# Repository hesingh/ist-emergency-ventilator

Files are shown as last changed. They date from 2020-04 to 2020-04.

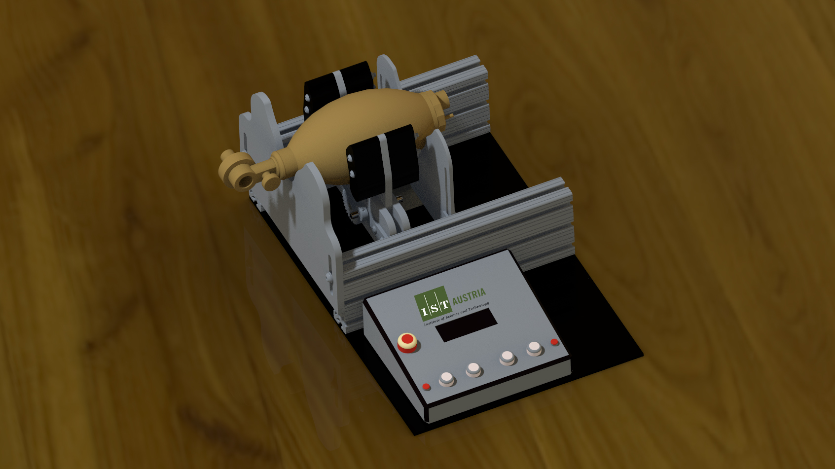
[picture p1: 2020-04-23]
Mechanical/Picture_3D_Model/bild_3_1.jpg

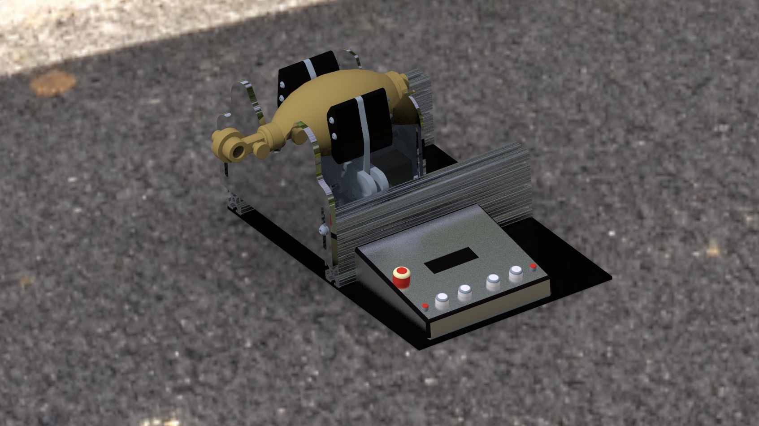
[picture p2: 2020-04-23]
Mechanical/Creo 6.0/creo.jpg

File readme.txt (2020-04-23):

ABOUT:
The enclosed files belong to the eVent IST ventilator project, inspired by the MIT E-Vent project (see https://e-vent.mit.edu/). We developed the ventilator system using technical documentation of MIT, infrastructure of IST AUSTIRA and consulting of three medical practitioners. We developed and built with great care and focus on stability and safety, still the device is not certified and not built according to all applicable regulations. Please note that this is work in progress and has never been tested on a human. The goal of the eVent IST ventilator project is to provide a simple and fast to replicate system for emergency response, and was created in reaction to the COVID-19 crisis early 2020. Furthermore, its intention is not to replace common ventilator systems, but to bridge a situation where not enough conventional machines are available.

ATTRIBUTION:
Please notice that the eVent IST ventilator was developed using the information shared by the Massachusetts Institute of Technology (MIT). You can find information on the original MIT E-Vent project under https://e-vent.mit.edu/. All Terms of Use, found here: https://e-vent.mit.edu/terms-and-conditions/, concerning the original MIT content do apply.
3rd party libraries used: Encoder by Paul Stoffregen (https://github.com/PaulStoffregen/Encoder), LiquidCrystal (https://github.com/arduino-libraries/LiquidCrystal).

FOLDERS:

	Folder name	Description							Origin
	------------------------------------------------------------------------------------------------
	Electronics	contains files for the electronic parts of the ventilator	mostly MIT E-Vent
	License		contains relevant license files					https://opensource.org
	Mechanical	contains files for the mechanical parts of the ventilator	mostly MIT E-Vent
	Pictures	contains pictures of the machine				IST AUSTRIA
	Software	contains files for the software of the ventilator		IST AUSTRIA

COPYRIGHT AND LICENSE: 
Selected Content may be downloaded by you pursuant to these Terms of Use. All copyright in and to the original MIT E-Vent Design Specifications belong to MIT. MIT is making the Design Specifications freely available to you to use, subject to these Terms of Use and your agreement to give full attribution to MIT should you reproduce, display, disseminate, or distribute the Design Specifications. All copyright in and to content going beyond the MIT E-Vent Design Specifications, and especially the software, belong to IST AUSTRIA. If and to the extent you provide any feedback, suggestions, recommendations, analysis or other information or data to IST in connection with your use of the Content (“Feedback”), you hereby permit IST to use, reproduce, disclose, distribute, modify, and prepare derivative works of such Feedback for any purpose whatsoever in perpetuity. Any downloadable software is subject to the MIT Open Source license, found here: https://opensource.org/licenses/MIT.
3rd party libraries included: Encoder: (MIT License), LiquidCrystal: LGPL License v3 (https://opensource.org/licenses/LGPL-3.0).

DISCLAIMER OF WARRANTIES
YOU ACKNOWLEDGE THAT THE CONTENT IS IN RESEARCH PHASE AND ALL OUTCOMES FROM USE OF THE CONTENT ARE NOT KNOWN. YOUR USE OF THE CONTENT, INCLUDING THE DESIGN SPECIFICATIONS AND THE SOFTWARE, IS AT YOUR OWN RISK. THE CONTENT, INCLUDING THE DESIGN SPECIFICATIONS AND THE SOFTWARE, ARE PROVIDED ON AN “AS IS” AND “AS AVAILABLE” BASIS. 
IST AUSTRIA, ON BEHALF OF ITSELF AND ITS COLLABORATORS, MAKES NO REPRESENTATIONS, WARRANTIES OR COVENANTS, WHETHER STATUTORY, EXPRESS, IMPLIED, BY COURSE OF COMMUNICATION OR DEALING, OR OTHERWISE WITH RESPECT TO THE CONTENT, INCLUDING THE DESIGN SPECIFICATIONS AND THE SOFTWARE, AND ANY RESULTING DEVICE.  IST AUSTRIA, ON BEHALF OF ITSELF AND ITS COLLABORATORS, SPECIFICALLY DISCLAIMS ANY WARRANTY WITH REGARD TO FITNESS FOR ANY PARTICULAR PURPOSE, MERCHANTABILITY OR NON-INFRINGEMENT.
WITHOUT LIMITING THE GENERALITY OF THE FOREGOING, IST AUSTRIA, ON BEHALF OF ITSELF AND ITS COLLABORATORS, MAKES NO WARRANTY OF ANY KIND THAT THE CONTENT, INCLUDING THE DESIGN SPECIFICATIONS AND THE SOFTWARE, AND ANY RESULTING DEVICE OR THE RESULTS OF THE USE OF SUCH DEVICE WILL MEET YOUR OR ANY THIRD PARTY’S REQUIREMENTS, OR ACHIEVE ANY INTENDED RESULT OR THAT THE USE OF THE DESIGN SPECIFICATIONS AND THE SOFTWARE TO MAKE A DEVICE WILL COMPLY WITH INTERNATIONAL, FEDERAL, STATE OR MUNICIPAL LAWS AND REGULATIONS REGARDING MEDICAL DEVICES OR MEDICAL USES.  YOU EXPRESSLY ACKNOWLEDGE AND AGREE THAT IST AUSTRIA, ON BEHALF OF ITSELF AND ITS COLLABORATORS, IS NOT RESPONSIBLE FOR ANY HEALTH PROBLEMS, INJURIES OR DEATH THAT MAY RESULT FROM YOUR OR ANY THIRD PARTY’S USE OF ANY DEVICE RESULTING FROM YOUR USE OF THE CONTENT, INCLUDING THE DESIGN SPECIFICATIONS AND THE SOFTWARE.  IT IS UNDERSTOOD THAT IST AUSTRIA DOES NOT PROVIDE MEDICAL OR OTHER HEALTH-RELATED ADVICE.     
IST AUSTRIA, ON BEHALF OF ITSELF AND ITS COLLABORATORS, DISCLAIMS ANY RESPONSIBILITY FOR OR ASSURANCES REGARDING THE QUALITY, FUNCTIONALITY, OR SAFETY OF ANY DEVICE RESULTING FROM YOUR USE OF THE CONTENT, INCLUDING THE DESIGN SPECIFICATIONS AND THE SOFTWARE, OR ANY DEFECT, ERRORS OR MALFUNCTION IN CONNECTION THEREWITH.  FURTHER, IST AUSTRIA, ON BEHALF OF ITSELF AND ITS COLLABORATORS, DISCLAIMS ANY RESPONSIBILITY FOR OR ASSURANCES REGARDING ANY COMMENTS, FEEDBACK, INFORMATION OR OTHER KNOW-HOW PROVIDED BY ANY USER. YOU RELY ON USER COMMENTS, FEEDBACK, INFORMATION AND/OR KNOW-HOW SOLELY AT YOUR OWN RISK. 
YOU UNDERSTAND AND ACKNOWLEDGE THAT: YOU ARE A LEARNED INDIVIDUAL THAT HAS HAD THE OPPORTUNITY TO OBTAIN ANY AND ALL INFORMATION RELEVANT TO THE USE OF ANY DEVICE RESULTING FROM YOUR USE OF THE CONTENT, INCLUDING THE DESIGN SPECIFICATIONS AND THE SOFTWARE; YOU HAVE NO OBLIGATION TO USE THE CONTENT, THE DESIGN SPECIFICATIONS AND THE SOFTWARE OR ANY DEVICE RESULTING THEREFROM AND YOU DO SO IN YOUR SOLE DISCRETION; YOU ARE RESPONSIBLE FOR DETERMINING THE DEGREE OF MONITORING OR OVERSIGHT THAT IS APPROPRIATE IN CONNECTION WITH PATIENT CARE AND THE USE OF ANY DEVICE RESULTING FROM YOUR USE OF THE CONTENT, INCLUDING THE DESIGN SPECIFICATIONS AND THE SOFTWARE; YOU HAVE ACCEPTED ALL RESPONSIBILITY AND IST AUSTRIA, ON BEHALF OF ITSELF AND ITS COLLABORATORS, RETAINS NO RESPONSIBILITY FOR YOUR USE OF ANY RESULTING DEVICE; AND YOU WILL COMPLY WITH ALL LAWS AND GOVERNMENTAL RULES, REGULATIONS AND GUIDELINES, INCLUDING ANY SAFETY PRECAUTIONS, THAT ARE APPLICABLE TO THE DEVICE OR THE USE THEREOF.
IST AUSTRIA does not guarantee or warrant that files available for downloading from the Internet or the Site will be free of viruses or other destructive code. NEITHER IST AUSTRIA NOR ANY PERSON ASSOCIATED WITH IST AUSTRIA MAKES ANY WARRANTY OR REPRESENTATION WITH RESPECT TO THE SECURITY, RELIABILITY, QUALITY, OR AVAILABILITY OF THE SITE AND THE CONTENT. IST AUSTRIA WILL NOT BE LIABLE FOR ANY LOSS OR DAMAGE CAUSED BY A DISTRIBUTED DENIAL-OF-SERVICE ATTACK, VIRUSES OR OTHER TECHNOLOGICALLY HARMFUL MATERIAL THAT MAY INFECT YOUR COMPUTER EQUIPMENT, COMPUTER PROGRAMS, DATA OR OTHER PROPRIETARY MATERIAL DUE TO YOUR USE OF THE CONTENT, YOUR DOWNLOADING OF ANY AVAILABLE CONTENT, OR YOUR USE OF ANY WEBSITE LINKED TO THE CONTENT.  

LIMITATION OF LIABILITY
TO THE FULLEST EXTENT ALLOWABLE BY LAW, IN NO EVENT WILL IST AUSTRIA, ITS TRUSTEES, DIRECTORS, OFFICERS, FACULTY, STUDENTS, EMPLOYEES, AGENTS, AFFILIATES, VOLUNTEERS, AND COLLABORATORS AND THEIR RESPECTIVE SUCCESSORS, HEIRS AND ASSIGNS BE LIABLE OR RESPONSIBLE FOR, OR INDEMNIFY YOU OR ANY THIRD PARTY FOR, DIRECT, INDIRECT, SPECIAL, INCIDENTAL, CONSEQUENTIAL, PUNITIVE OR EXEMPLARY DAMAGES OF ANY KIND, UNDER ANY LEGAL THEORY, ARISING OUT OF OR IN CONNECTION WITH YOUR USE, OR INABILITY TO USE, THE CONTENT (INCLUDING THE DESIGN SPECIFICATIONS AND THE SOFTWARE), ANY WEBSITES LINKED TO THE SITE OR CONTENT OR ANY INFORMATION OBTAINED THROUGH THE CONTENT OR SUCH THIRD PARTY WEBSITES (INCLUDING BUT NOT LIMITED TO COMMENTS, FEEDBACK, INFORMATION AND KNOW-HOW FROM OTHER USERS); ANY USE OF A RESULTING DEVICE; ANY ERROR, FAILURE OR DEFECT OF SUCH DEVICE; OR ANY HARM OR INJURY CAUSED BY SUCH DEVICE.

INDEMNIFICATION
To the fullest extent permitted by law, you shall indemnify IST AUSTRIA and all of its trustees, directors, officers, faculty, students, employees, agents, affiliates, volunteers, and collaborators and their respective successors, heirs and assigns (collectively, the “Indemnified Parties”) from and against any and all losses and liabilities, including, without limitation, reasonable attorneys’ fees incurred by the Indemnified Parties in connection with any claim arising from or related to your breach of these Terms of Use, your use of, or inability to use, the Content and your use of any information obtained through use of the Site and Content. You shall cooperate as fully as reasonably required in the defense of any such claim.

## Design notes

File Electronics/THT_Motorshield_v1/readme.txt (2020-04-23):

The pins of the unused channel on the motor shield, need to be removed. 
There will be a SMD version with onboard motor controller soon.

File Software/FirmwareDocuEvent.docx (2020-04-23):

# Documentation eVent IST Firmware

# 1 Modes

Automated operation of ventilation bags in two Modes:

- Volume controlled ventilation with adjustable Parameters:

Parameter | Range | Unit
Volume | 300 - 900 | mL
Breath rate | 8 – 40 | Breaths per minute
Inspiratory : Expiratory ratio | 1:1 – 1:4

Table 1 - volume control parameters

- Pressure controlled ventilation with adjustable Parameters:

Parameter | Range | Unit
Pressure | 10 - 30 | mBar
Breath rate | 8 – 40 | Breaths per minute
Inspiratory : Expiratory ratio | 1:1 – 1:4

Table 2 - pressure control parameters

# 2 Pinout

The firmware is designed for an Arduino Mega. Nevertheless, the hardware should be compatible with the MIT project, which uses an Arduino Uno, because all mandatory functions have been mapped to Uno pins. The used pins are defined in the pins.h file.

Definition | Pin | Configuration | Description
LCD_D7 | 0 | digital output | LCD data line
LCD_D5 | 1 | digital output | LCD data line
ENC_A | 2 | digital input (INT)° | encoder impulse signal A
MOTOR_PWM | 3 | PWM output | defines speed of motor
LCD_D4 | 4 | digital output | LCD data line
LCD_ENABLE | 5 | digital output | LCD control signal
LCD_RS | 6 | digital output | LCD control signal
LCD_D6 | 7 | digital output | LCD data line
CONFIRM_BUTTON | 8 | digital input (DB*) | momentary button to confirm
BUZZER | 9 | PWM output | piezo buzzer
ENC_B | 10 | digital input | encoder impulse signal B
SILENCE_BUTTON | 11 | digital input (DB*) | momentary button to mute alarms
MOTOR_DIR | 12 | digital output | defines direction of motor
LIMIT_SWITCH | 13 | digital input | state of the limit switch, defines home
VOL_POT | A0 | analog input | sets volume setpoint
RATE_POT | A1 | analog input | sets breath rate setpoint
I2E_POT | A2 | analog input | sets inspiration/expiration ratio setpoint
PRS_POT | A3 | analog input | Sets maximum pressure setpoint
MODE_SWITCH | A4 | analog input | three states: VCC | VCC/2 | GND
PRESSURE | A5 | analog input | signal of pressure sensor 0.2-4.7V
LCD_BACKLIGHT | 14 | digital output | LCD backlight on/off via transistor
LED_POWER | 15 | digital output | LED to indicate that Arduino booted
LED_GREEN | 16 | digital output | LED to indicate active mode
LED_RED | 17 | digital output | LED to indicate error
ENC_I | 18 | digital input | not implemented
MOTOR_SENSE | A8 | analog input | measure motor current (1.65V/A)
MOTOR_BRAKE | A9 | digital output | not implemented

Table 3 - pinout

*debouncing necessary °Interrupt

# 3 States

In the states.h file, the states of switches, buttons and the motor are defined to provide easy adjustment to different electrical implementation. For example, one might use external pull-down resistors instead of the internal pull-ups, then it would be necessary to change the “BUTTON_PRESSED” state to “HIGH”. Or normally-closed buttons or switches are used instead of the normally-open switches we used.

# 4 Variables

A number of constants in main.cpp are defined. They are used to adjust the firmware to parameters of the electro-mechanical construction. Moreover, some clinical process-related constants are set.

Name | Unit | Description
maxMotorCurrent | mA | if this current is exceeded the motor will be stopped
diffBagPosition | T* | ticks between home and fingers touching the bag
timeHold | ms | time between inhale and exhale
pressurePlateauMax | mbar | maximum pressure between inhale and exhale
velocityHoming | DCS° | defines the motor speed while homing
controlPeriod | ms | period time of the velocity controller

Table 4 - constants

The following tables describe the used variables separated into functional groups.

Name | Unit | Description
lastMode | | the mode which was active before the current mode
mode | | the current mode
nextMode | | the mode which should be active after the current mode
state | | the current state in the state machine

Table 5 - state machine variables

Name | Unit | Description
homePosition | T* | encoder value at the position of the limit switch
currentPosition | T* | last encoder reading
bagPosition | T* | position where fingers touching the bag
inhaleEndPosition | T* | position at the end of the inspiratory phase
prePeriodPosition | T* | ticks before the current velocity control period

Table 6 - positioon variables

Name | Unit | Description
volumeTidalSet | mL | unconfirmed set value for volume tidal
breathsPerMinuteSet | 1/min | unconfirmed set value for the breath rate
I2E_ratioSet | | unconfirmed set value for the I:E ratio
limitPressureSet | mBar | unconfirmed set value for the pressure limit
lastVolumeTidalSet | mL | last unconfirmed set value for volume tidal
lastBreathsPerMinuteSet | 1/min | last unconfirmed set value for the breath rate
lastI2E_ratioSet | | last unconfirmed set value for the I:E ratio
lastLimitPressureSet | mBar | last unconfirmed set value for the pressure limit

Table 7 - set - potentiometer variables

Name | Unit | Description
breathsPerMinute | 1/min | breaths per minute, also called respiratory rate (RR)
I2E_ratio | | ratio of inhale to exhale time

Table 8 - clincal variabels

Name | Unit | Description
targetTimeInhale | ms | calculated length of the inspiratory phase
targetTimeExhale | ms | calculated length of the expiratory phase
volumeTidal | mL | total volume delivered to the patient
volumeTicks | T* | encoder ticks necessary to deliver the volume

Table 9 - volume mode variables

Name | Unit | Description
currentFlow | ml/s | calculated flow in last controller period
targetFlow | ml/s | flow which should be reached according to calculations
meanFlow | ml/s | mean flow which should be reached over whole inspiration
targetInhaleVelocity | T*/s | target input of controller for inspiratory phase
targetExhaleVelocity | T*/s | target input of controller for expiratory phase
currentVelocity | T*/s | measure input of controller
dutyCycleOutput | DCS° | output of controller, scaled from 0-255 for PWM Output
integral | | integral value for I- controller
iTerm | | I factor of controller
pTerm | | P factor of controller

Table 10 - controller variables

Name | Unit | Description
pressurePlateau | mbar | Last measured plateau pressure (between I and E phase)
limitPressure | mbar | set limit pressure

Table 11 - pressure variables

* Ticks °Duty Cycle Steps

Additionally, several timer variables are used to handle non-blocking timing in the state machine.

# 5 Calculations

## 5.1 Volume

To identify the relation between the encoder steps moved, and the volume delivered to the patient, a test was performed. While varying the encoder distance, the delivered volume was measured with a lung simulator “Dräger LS800”. A “Laerdal bag adult” and an encoder with a resolution of 500 steps per rotation was used.

As the results were very close to linear, a model of two linear functions was considered reasonable to define the relation.

Volume[mL]=Steps*8-190 | for Steps<60

Volume[mL]=Steps*12-420 | for Steps>60

Figure 1 – Pumped air volume per step

## 5.2 Inhale/Exhale Time

The inhale/exhale time is calculated with the user defined parameters breath rate and I:E ratio.

T_(single breath) [ms]=60000/(breath rate)-T_(hold) | T_(hold) …break between I and E

T_(inhale) =T_(single breath) *1/(1+ I:E) | Example I:E=1:2→ T_(single breath) *1/(1+2)

T_(exhale) = T_(single breath) - T_(inhale)

## 5.3 Velocity

To be able to control the velocity, the current velocity is calculated with the covered encoder steps in the last time period.

velocity [T/s]=Ticks[T/P]*1000/(P[ms])

## 5.4 Flow

Despite the flow is not measured by the system, it should be controlled to provide an accelerating behaviour at the inspiration phase of the volume control ventilation. For that reason, it is calculated based on the calculated volume over a known time period.

flow[(ml)/s]=velocity[T/s]*8 or flow=velocity*12 , depending on position

The flow should be slowly increased and then stay constant till the end of the inspiration. However, the mean flow over one inspiration phase has to be met to attain the required inhale time.

flow_(mean) =(Volume[T])/(Time_(inhale) [s])*12

It was defined that the inspiration should start with 20% of the mean flow. It then increase linear till half the inhale time is reached. To accomplish that, the following model is used to calculate the current target flow.

flow=flow_(mean) *(0.2 +(1.1 * CC)/(0.5 * CC_(max))) | CC→Control Cycle<(CC_(max))/2

flow=flow_(mean) *1.3 | CC→Control Cycle>(CC_(max))/2

Figure 2 – Flow model

(fmean = 30 L/min)

# 6 Controller

To control the velocity and pressure, a PI controller was implemented. To achieve that, the function “controlInhaleVelocity” (or exhale) and “controlPressure” is called after every control period. The control period is defined by the constant “controlPeriod” and is hardcoded to be 50ms.

The controller calculates the control difference and adjusts the PWM output, which controls the speed of the motor, depending on the “pTerm” and “iTerm” settings. The preconfigured values for the control terms have been chosen by testing with a lung simulator “Dräger LS800”. They may vary depending on the used motor. More information about PI controllers can be found on https://en.wikipedia.org/wiki/PID_controller#PI_controller.

# 7 State Machine

The firmware differs between 4 modes:

- Idle
- Homing
- Volume
- Pressure

The user can select between idle, volume-controlled ventilation and pressure-controlled ventilation. Every ventilation mode starts with a homing sequence to calibrate the positions.

The state machine is mainly designed after the concept of MIT which, at the moment of writing, can be found at: https://e-vent.mit.edu/controls/high-level-controls/

State | Action | Condition
0 | Move fingers outwards | Limit switch reached?
1 | Move fingers inwards, set home position | Limit switch not reached?
2 | Move to bag position | Bag position reached?

Table 12- Homing states

State | Action | Condition
0 | start homing | homing done?
1 | move fingers inhale, control velocity | Inhale end position reached? Start timer
2 | reset control parameters for exhale | Time hold reached?
3 | move fingers exhale, control velocity | bag position reached?
4 | stop, wait for rest of single breath time | Breath time reached?

Table 13 - Volume states

State | Action | Condition
0 | start homing | homing done?
1 | move fingers inhale, control pressure | Inhale time or close position reached?
2 | reset control parameters for exhale | Time hold reached?
3 | move fingers exhale, control velocity | bag position reached?
4 | stop, wait for rest of single breath time | Breath time reached?

Table 14 - Pressure states

# 8 Alarms

Alarm | Reason
LOW VOLUME | The minute-volume in pressure mode fell below the hardcoded minute-volume minimum. (minVolumeperMinute in alarms.cpp, def: 3Liters)
MOTOR ERR | Either the motor is unplugged or blocked. Alarm occurs if the current exceeds the hardcoded maximum motor current or the motor was not able to move for 2 seconds. (maxMotorCurrent in alarms.cpp, def: 2000mA)
PRES ERR | The pressure is either too high or too low. High pressure would indicate a bad compliance of the lung, low pressure would indicate leakage. (pressurePlateauMax, pressureMax, pressureMin in alarms.cpp)

To make the alarm louder, simply replace the “tone()” functions through “digitalWrite(BUZZER, HIGH) and “noTone()” to digitalWrite(BUZZER, LOW).

# 9 Installation Guide

There are two different software versions included in the project. First, an Arduino IDE project file (.ino). You can use this file, if you have a similar electromechanical setup and just want to flash your Arduino without editing the project. The advantage of the Arduino IDE is, that it is very easy to get started. The disadvantage is, that the structure of an Arduino .ino file does support separating the code into different files. Therefore, the structure of the code is very confusing, and it is hard to do any changes.

The Atom IDE project is more complicated to install but provides a more structured view of the code.

## 9.1 Arduino IDE

1. Download and install Arduino IDE: https://www.arduino.cc/en/main/software
2. Open the .ino file with Arduino IDE.
3. Connect the Arduino to the PC via the USB cable.
4. In the IDE under “Tools” select the port with your Arduino.
5. Click Upload

## 9.2 Atom IDE

1. Download and install Atom IDE: https://atom.io/ (you will need to install Python 2.7 as well)
2. In Atom, open the package manager (File/Setting/Install) and install Platformio-ide
3. When restarting Atom, the platform io home screen should appear. Press Open Project and find the eVent Folder on your PC.
4. Connect the Arduino to the PC via the USB cable.
5. Select Upload from toolbar on the left side.

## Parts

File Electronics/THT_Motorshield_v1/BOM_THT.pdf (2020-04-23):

| | | | Pcs total | | Price total €
| | | | 138 | | 670.315
Name | Supplier | Supplier Nr | Manu. Nr | Pcs | Price | Total
20x4 LCD | RS Components | 532-6824 | 204A-GC-BC-3LP | 1 | 9.96 | 9.96
10k Potentiometer LCD | RS Components | 521-9647 | 3296W-1-103LF | 1 | 1.5 | 1.5
330 Ohm Resistor LCD | RS Components | 214-1068 | ROX1SJ330R | 1 | 0.145 | 0.145
Potentiometer 10k linear | RS Components | 789-9438 | 91A1A-B28-A15L | 4 | 5.03 | 20.12
Knob Potentiometer | RS Components | 498-902 | | 4 | 2.71 | 10.84
Motor | RS Components | 877-7180 | P205-24-100 | 1 | 185.04 | 185.04
Snap Action Limit Switch Roller Lever | RS Components | 386-0423 | Z15GW2BOMI | 1 | 7.51 | 7.51
Pressure sensor 10kPa | RS Components | 922-7409 | MPXV5010DP | 1 | 8.39 | 8.39
DC Power Socket 2.5mm | RS Components | 705-1525 | L712AS | 1 | 8.82 | 8.82
24V Power Supply | RS Components | 831-9157 | GSM90B24-P1M | 1 | 58.73 | 58.73
Encoder | RS Components | 818-8820 | HEDL-5540#A11 | 1 | 27.99 | 27.99
Emergency button | RS Components | 690-6954 | 84-5030.0040 | 1 | 36.22 | 36.22
Mode Switch | RS Components | 495-4377 | 1-1634201-2 | 1 | 2.15 | 2.15
On/off switch | RS Components | 607-7781 | 1935.3118 | 1 | 5.61 | 5.61
Momentary Push Button Switch quit/confirm | RS Components | 690-3255 | R16FFNSTAG | 2 | 5.39 | 10.78
LED green | RS Components | 700-1546 | 700-1546 | 2 | 2.36 | 4.72
LED red | RS Components | 700-1542 | 700-1542 | 1 | 2.42 | 2.42
Buzzer Piezo | RS Components | 724-3178 | 724-3178 | 1 | 1.95 | 1.95
NPN 3904 | RS Components | 739-0442 | 2N3904TA | 10 | 0.173 | 1.73
Resistor | RS Components | 707-7666 | 707-7666 | 10 | 0.09 | 0.9
Microswitch silver | RS Components | 515-779 | V15T16-CZ100A02 | 1 | 3.46 | 3.46
Microswitch black | RS Components | 159-4590 | DB1C-A1LB | 1 | 3.23 | 3.23
3 Pole Din Plug Plug | RS Components | 533-6720 | SV 30 | 1 | 2.93 | 2.93
KFV 3 Pole Din Socket Socket | RS Components | 533-4825 | KFV 30 | 1 | 2.39 | 2.39
SV 5 Pole Din Plug Plug Motor | RS Components | 533-2885 | SV50/6 | 1 | 3.65 | 3.65
KFV 5 Pole Din Socket Socket Motor | RS Components | 533-2712 | KFV 50/6 | 1 | 2.6 | 2.6
220µ Electrolytic Capacitor | RS Components | 315-0726 | EEUFC1V221 | 2 | 0.27 | 0.54
Housing | RS Components | 704-3940 | 92865250.MT6 | 1 | 27.7 | 27.7
Recom Through Hole Switching Regulator 7805 | RS Components | 416-874 | R-78HB5.0-0.5 | 1 | 8.29 | 8.29
Arduino Motor Shield | RS Components | 182-5518 | A000079 | 1 | 18.58 | 18.58

Arduino Uno | RS Components | 715-4081 | A000066
1 | 19.13 | 19.13
Arduino Shield | RS Components | 176-3652 | TSX00083
1 | 10.08 | 10.08
Single Pole Single Throw | RS Components | 891-9832 | -
2 | 3.8 | 7.6
Pneumatic Bulkhead Threaded Adapter | RS Components | 367-6199 | 0920 00 13
1 | 9.56 | 9.56
Threaded-to-Tube Pneumatic Fitting | RS Components | 146-5208 | 0191 04 13
2 | 61.05 | 122.1
USB Adapter Panel Mount | RS Components | 907-5628 | 907-5628
1 | 8.06 | 8.06
USB A B cabel | RS Components | 411-176 | 11.02.8808-50
2 | 2.07 | 4.14
M20 Straight Pin Header | RS Components | 547-3150 | M20-9993645
5 | 2.15 | 10.75
Buzzer 24V | RS Components | 457-055
1 | 2.01 | 2.01

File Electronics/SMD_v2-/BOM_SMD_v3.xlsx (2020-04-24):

 |  |  |  | Pcs total |  | Price total
 |  |  |  | 82 |  | 553.331
Name | Supplier | Supplier Nr | Manu. Nr | Pcs | Price | Total
20x4 LCD | RS | 532-6824 | 204A-GC-BC-3LP | 1 | 9.96 | 9.96
10k Poti LCD | RS | 521-9647 | 3296W-1-103LF | 1 | 1.5 | 1.5
330 Ohm Widerstand SMD | RS | 223-0354 | CRG0805F330R | 9 | 0.031 | 0.279
10k Ohm Widerstand SMD | RS | 125-1189 | CRG0805F10K | 5 | 0.005 | 0.025
1k Ohm Widerstand SMD | RS | 223-0427 | CRG0805F1K0 | 1 | 0.038 | 0.038
0.15 Ohm Widerstand SMD | RS | 721-5886 | ERJ8BSFR15V | 1 | 0.388 | 0.388
Poti 10k linear | RS | 789-9438 | 91A1A-B28-A15L | 4 | 5.03 | 20.12
Knopf Poti | RS | 498-902 | 498-902 | 4 | 2.71 | 10.84
Motor 1 | RS | 877-7180 | P205-24-100 | 1 | 185.04 | 185.04
Drucksensor 10kPa SMD | RS | 922-7409 | MPXV5010DP | 1 | 8.39 | 8.39
DC Buchse 2.5mm verriegelbar | RS | 705-1525 | L712AS | 1 | 8.82 | 8.82
24V Netzteil | RS | 831-9157 | GSM90B24-P1M | 1 | 58.73 | 58.73
Encoder 4mm Hohlwelle | RS | 818-8820 | HEDL-5540#A11 | 1 | 27.99 | 27.99
Fuse holder PCB mount | RS | 176-9047 | 31.8201 | 1 | 0.535 | 0.535
Fuse 5x20mm T2A | RS | 563-722 | 563-722 | 1 | 0.18 | 0.18
Not Aus Schalter | RS | 690-6954 | 84-5030.0040 | 1 | 36.22 | 36.22
LED grün | RS | 700-1546 | 700-1546 | 2 | 2.36 | 4.72
LED rot | RS | 700-1542 | 700-1542 | 1 | 2.42 | 2.42
Buzzer Piezo | RS | 724-3178 | 724-3178 | 1 | 1.95 | 1.95
NPN 3904 SMD | RS | 725-8616 | MMBT3904,215 | 5 | 0.067 | 0.335
Motor Stecker 5Pol | RS | 533-2885 | SV50/6 | 1 | 3.65 | 3.65
Motor Buchse 5Pol | RS | 533-2712 | KFV 50/6 | 1 | 2.6 | 2.6
10µ Elko SMD | RS | 103-4182 | UMK325AB7106KM-P | 7 | 0.58 | 4.06
100n 0805 Ko | RS | 464-6688 | 08055C104KAT2A | 7 | 0.031 | 0.217
Gehäuse | RS | 704-3940 | 92865250.MT6 | 1 | 27.7 | 27.7
DCDC 7805 | RS | 416-874 | R-78HB5.0-0.5 | 1 | 8.29 | 8.29
Arduino Mega 2560 | RS | 715-4084 | A000067 | 1 | 41.26 | 41.26
Drucktaster | RS | 891-9832 | 891-9832 | 2 | 3.8 | 7.6
USB Adapter Tafelmontage | RS | 907-5628 | 907-5628 | 1 | 8.06 | 8.06
USB A B Kabel | RS | 411-176 | 11.02.8808-50 | 2 | 2.07 | 4.14
Stiftleiste | RS | 547-3150 | M20-9993645 | 5 | 2.15 | 10.75
EIN/AUS Schalter | RS | 394-419 | 394-419 | 1 | 2.83 | 2.83
Moi Umschalter 3 Stellung | RS | 190-0658 | 5639A | 1 | 6.04 | 6.04
Endschalter | RS | 515-779 | V15T16-CZ100A02 | 1 | 5.08 | 5.08
O2 4mm Pushfit Schottverschraubung | RS | 176-1296 | 176-1296 | 1 | 4.62 | 4.62
Bundbuchse 10mm | Conrad | 237430 - 62 | BB101608SINT | 4 | 1.66 | 6.64
dc hohlstecker verriegelbar | RS | 878-7216 | 761KS17 | 1 | 5.54 | 5.54
molex stecker passend für conrad motor | RS | 679-5681 | 26-60-4020 | 1 | 0.179 | 0.179
decoder stecker passend für conrad motor | RS | 820-1434 | B4B-PH-K-S(LF)(SN) | 1 | 0.341 | 0.341
Motortreiber | RS | 714-7715 | L298P | 1 | 4.73 | 4.73
OPV AD822 | RS | 412-472 | AD822BRZ | 1 | 11.06 | 11.06
Diode Schottky 1A | RS | 743-6009 | SS14L R3 | 4 | 0.077 | 0.308
Kühlkörper | RS | 867-9039 | RPI-COOLINGKIT.9 | 1 | 2.783 | 2.783
 | https://www.rs-online.com/
 | https://www.conrad.com/

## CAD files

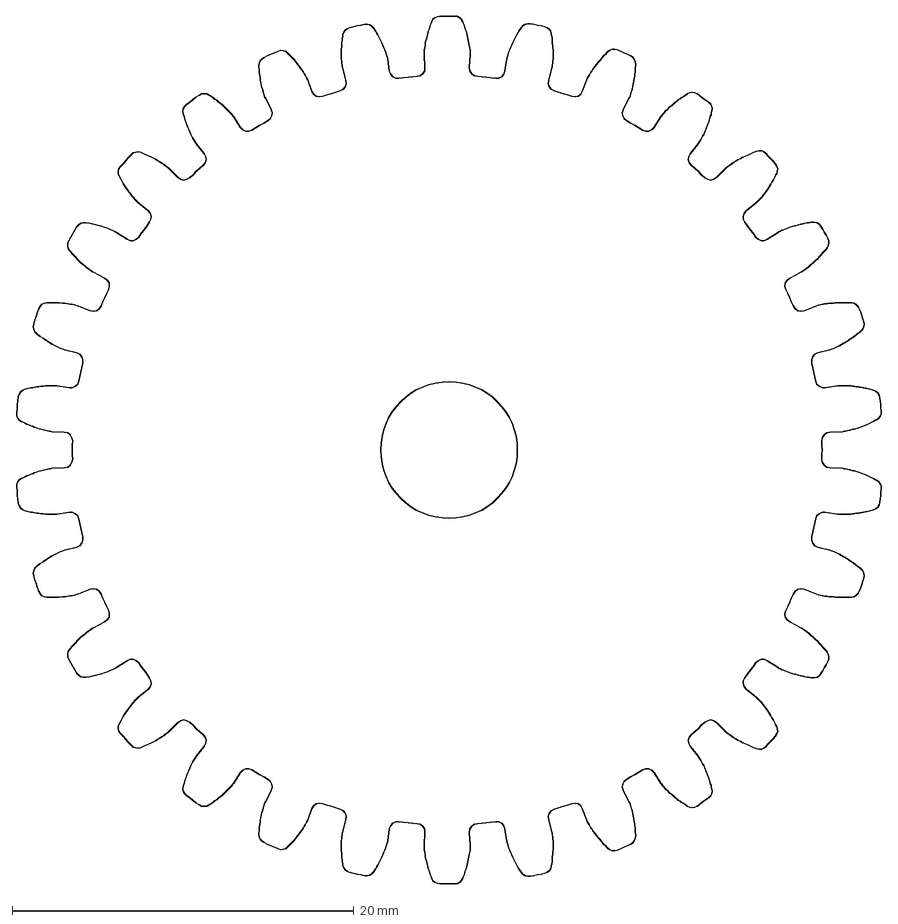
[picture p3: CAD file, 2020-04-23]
Mechanical/Creo 6.0/drive_gear_-_thickness_assumed.dxf
50.6 x 50.8 mm

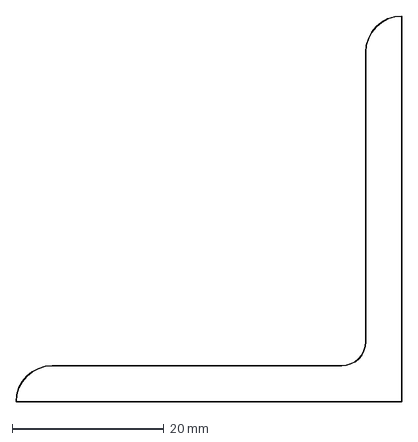
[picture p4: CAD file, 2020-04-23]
Mechanical/DXF/copy_of_47065t239_aluminum_t-sl.dxf
50.8 x 50.8 mm

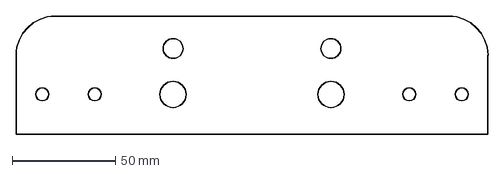
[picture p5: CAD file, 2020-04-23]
Mechanical/DXF/finger_mount_-_thickness_assume.dxf
228.6 x 57.2 mm

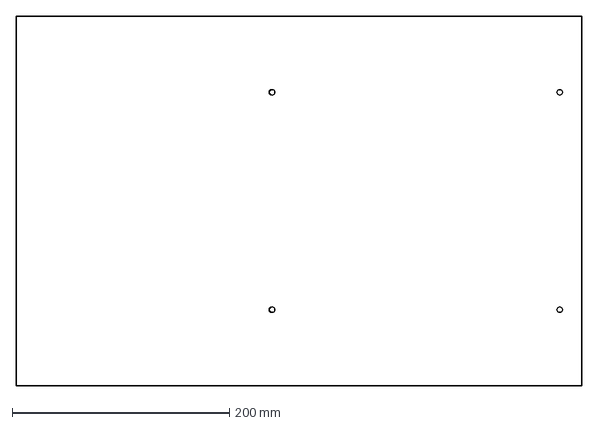
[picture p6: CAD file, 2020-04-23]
Mechanical/DXF/unterplatte.dxf
520.0 x 340.0 mm

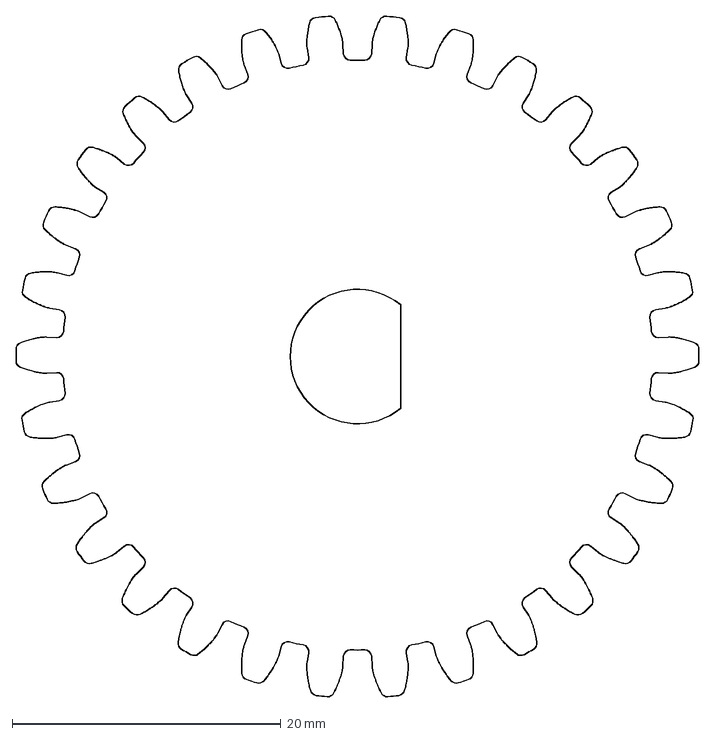
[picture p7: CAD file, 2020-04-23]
Mechanical/DXF/drive_gear_-_thickness_assumed.dxf
50.8 x 50.6 mm

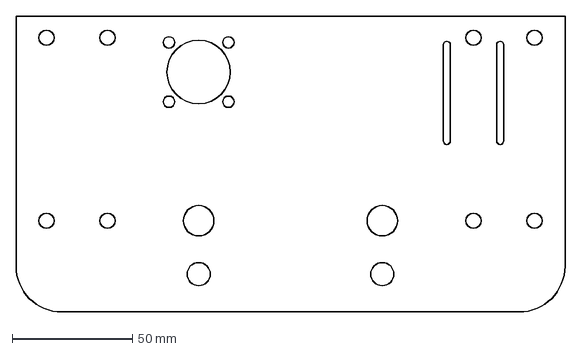
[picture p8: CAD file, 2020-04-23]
Mechanical/DXF/motor_and_finger_mount.dxf
228.6 x 123.2 mm

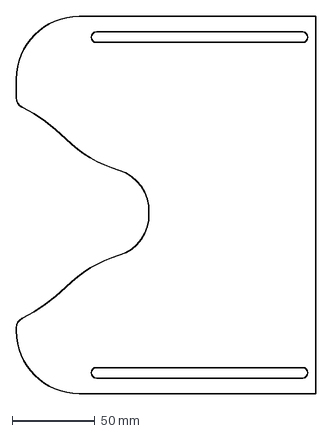
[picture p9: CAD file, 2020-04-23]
Mechanical/DXF/backplate.dxf
181.2 x 228.6 mm

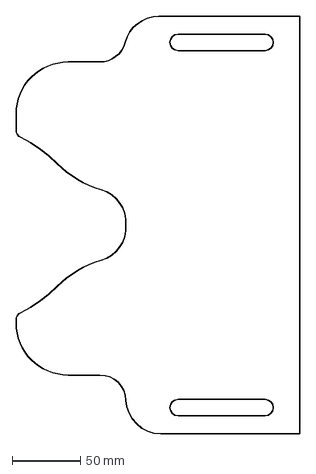
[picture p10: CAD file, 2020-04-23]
Mechanical/DXF/frontplate.dxf
207.3 x 304.8 mm

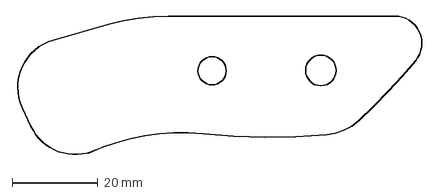
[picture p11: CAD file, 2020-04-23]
Mechanical/DXF/finger_tip_-_thickness_assumed.dxf
95.1 x 32.7 mm

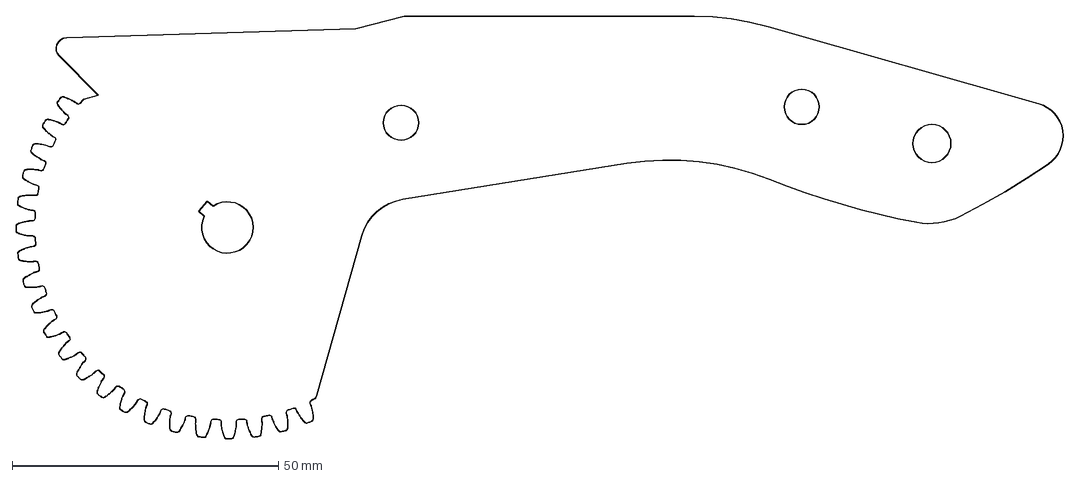
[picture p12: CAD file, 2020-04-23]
Mechanical/DXF/finger_-_thickness_assumed.dxf
197.0 x 79.4 mm

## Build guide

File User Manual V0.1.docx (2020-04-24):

User Manual of IST Austria Emergency Ventilator

V0.1

Last updated:

24.04.2020

Electronic Workshop

Institute of Science and Technology Austria

T +43-(0)2243 9000-1055

Am Campus 1

A-3400 Klosterneuburg

Written by:

Abdulhamid Baghdadi (abdulhamid.baghdadi@ist.ac.at)

Daniel Waldhäusl (daniel.waldhAeusl@ist.ac.at)

Table of Contents

# 1. Description

This respirator is based upon the idea of pressing an ambu bag, which can be removed and operated manually in case the respirator fails. There are two operation modes: controlled-volume and controlled-pressure respiration. The first mode provides a controlled volume of air to the patient in a set amount of time, while the second maintains a set airway pressure for a given inspiratory time. For more details about the operation modes, please refer to the firmware documentation.

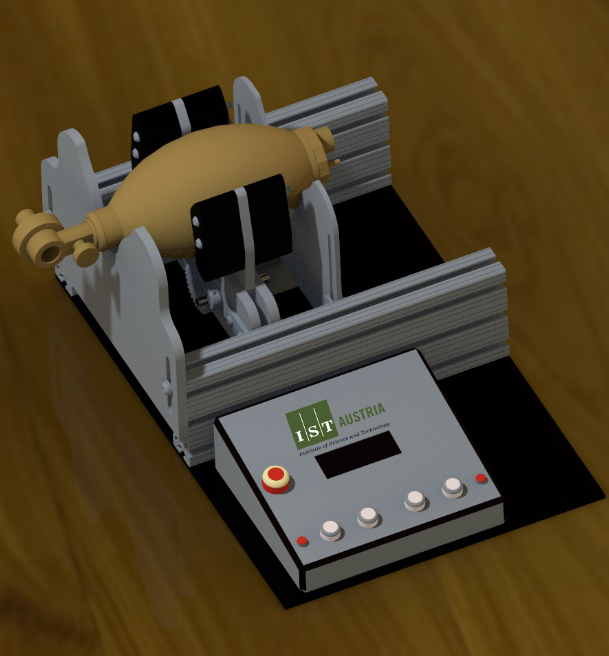
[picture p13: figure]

Figure 1 - IST Austria Emergency Ventilator

The following parameters are adjustable:

Parameter | Range | Unit
Volume* | 300 - 900 | mL
Breath rate | 8 – 40 | Breaths per minute
Inspiratory : Expiratory ratio | 1:1 – 1:4
Threshold pressure** | 10 - 30 | mBar

Table 1 – Control Parameters

*applies only to the controlled-volume mode

**applies only to the controlled-pressure mode

# 2. Controller Box

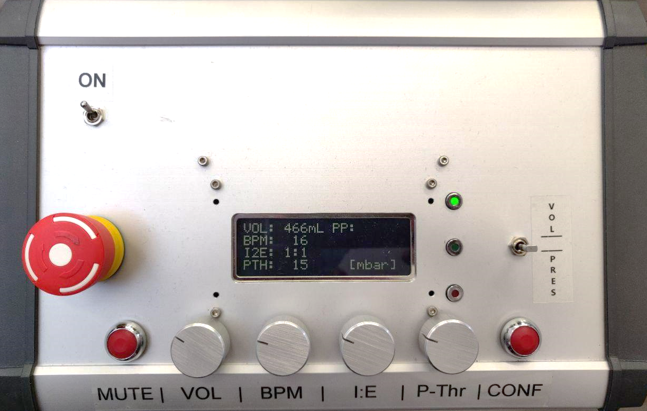
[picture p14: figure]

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
1. Power switch.
2. Emergency button.
3. Mute button: shuts the alarm off for 3 seconds.
4. VOL control knob: sets the value of the breath volume in mL.
5. BPM control knob: sets the breath-per-minute rate.
6. I:E control knob: sets the inhale-to-exhale rate.
7. P-Thr control Knob: sets the pressure threshold value. This value only affects the operation in pressure-control mode.
8. CONF button: confirms the recent change of parameters. If this button is not pressed after changes, parameter changes have no effect and the screen will start blinking until this button is pressed.
9. Alarm indicator: Lights red when an error occurs. Description of the error will appear of the screen (see chapter 4. Alarms).
10. Operation indicator: lights green when the respirator is running (not in idle mode).
11. Power indicator: lights green when the power supply is connected.
12. Mode switch: switches the respirator between volume control, pressure control or idle mode.
13. PP OR volume: depending on the operation mode, this indicator might read PP (Peak Pressure) or Volume. In volume-control mode, “PP” shows the maximum pressure that was reached in the last cycle, which means, that this value will be updated by the end of each cycle. In pressure-controlled mode, “Volume” shows the volume inhaled in the last cycle.

# 3. Operation

1) Plug in the 24V power supply cable.
2) Make sure the air pipe socket on the side of the controller box is connected through a rigid air tube to the designated place for measuring air pressure in the ventilation system.
3) Make sure the mode switch is standing on the idle mode; otherwise, the ventilator will start working as soon as the power is switched on.
4) Switch the power on. If the controller does not power up, make sure the emergency button is not pressed.
5) Adjust the needed parameters using the control knobs, then click confirm when ready.
6) Move the mode switch to the desired mode.
7) In case an alarm goes up, start ventilating the patient manually and check chapter 4. Alarms to see the cause for the alarm

# 4. Alarms

The following errors will cause the alarm to go off and will be visible on the screen until the error cause is eliminated. To stop the buzzer, please click on the MUTE button.

Alarm | Reason
LOW VOLUME | The minute-volume in pressure mode fell below the hardcoded minute-volume minimum.
MOTOR ERR | The motor is either unplugged or blocked. Alarm occurs if the current exceeds the hardcoded maximum motor current or the motor was not able to move for 2 seconds.
PRES ERR | The pressure is either too high or too low. High pressure would indicate a bad compliance of the lung, low pressure would indicate leakage.

Table 2 - Alarms

# 5. Safety Measures

1. Keep the ambu-bag easily removable for manual respiration in case of emergency
2. If alarm goes up, use the bag manually and call for help to fix the cause for the alarm
3. Make sure every individual around the respirator is familiar with its operation principles or at least the sound of the alarm.

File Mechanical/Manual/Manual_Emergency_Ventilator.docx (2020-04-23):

Emergency Ventilator

Mechanical Production:

We use this machinery for the production:

Laser Cutter, Water Cutter, Lathe, Milling Machine,

Assembly: mit_e_vent_t-slot

1. 120x40x340mm Item Profiles (2Pieces) → Front 1xM8 Thread
2. „Unterplatte“ made from acrylic (5-6mm) (1Piece)
  a. Laser Cutting
3. „Frontplate“ made from acrylic (10mm) (1Piece)
  a. Laser Cutting
4. „Backplate“ made from acrylic (8-10mm) (1Piece)
  a. Laser Cutting
5. „Aluminium_T-SL“ made from aluminium (8Pieces)
  a. Water Cutting and Milling Machine
6. „Motor_and_Finger_Mount“ made from aluminium (10mm) (1Piece)
  a. Water Cutting and Milling Machine
7. „Finger_Mount“ made from aluminium (10mm) (1Piece)
  a. Water Cutting and Milling Machine
8. „Finger“ made from aluminium (10mm) (2Pieces)
  a. Water Cutting
9. „Drivegear“ made from aluminium (10mm) (1Pieces)
  a. Water Cutting and Milling Machine
10. „Finger_Tip“ made from acrylic (10mm) (16Pieces)

Source: https://e-vent.mit.edu/

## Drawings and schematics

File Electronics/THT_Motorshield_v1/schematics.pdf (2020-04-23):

# 2N3904 F/BC352.54MM 330

# GND ⁺⁵V

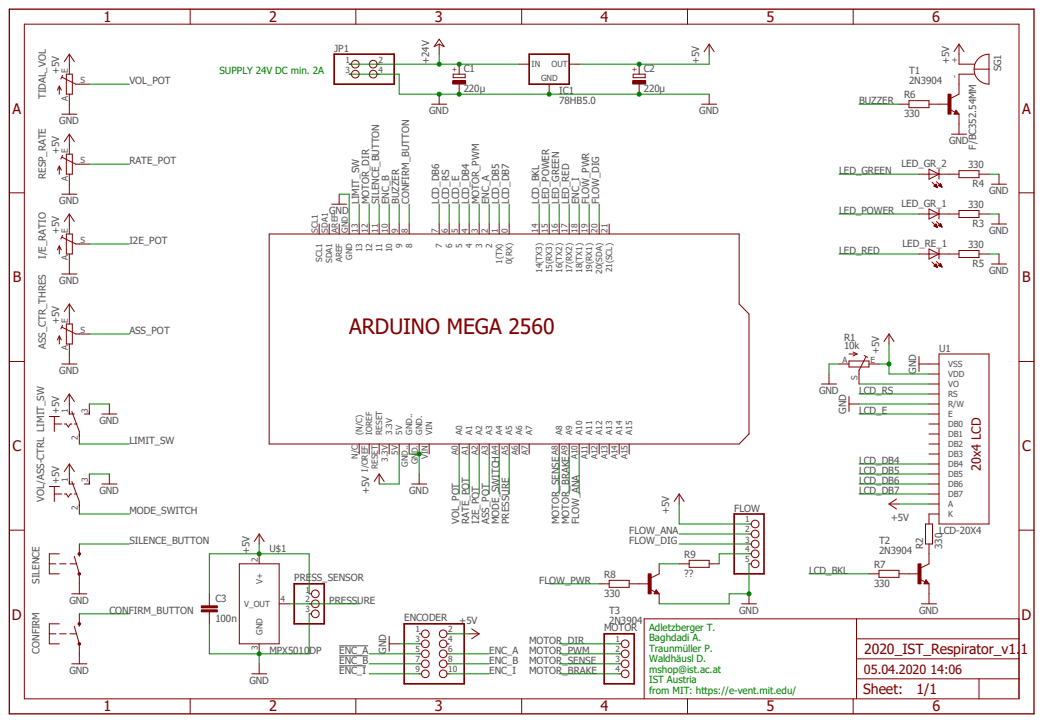
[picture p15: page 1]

S TIDAL_VOL A E S RESP_RATE A E S I/E_RATIO A E S ASS_CTR_THRES A E S LIMIT_SW
LCD-20X4 ⁺⁵V +⁵V +⁵V +⁵V +⁵V +⁵V

2 1(TX) 1 0(RX) 0 A5 A5 A4 A4 A3 A3 A2 A2 A1 A1 A0 A0 VIN VIN GND. GND. GND.. GND.. 5V 5V 3.3V 3.3V RESET RESET IOREF I/OREF (N/C) N/C 14(TX3) 14 15(RX3) 15 16(TX2) 16 17(RX2) 17 18(TX1) 18 19(RX1) 19 20(SDA) 20 21(SCL) 21 A15 A15 A14 A14 A13 A13 A12 A12 A11 A11 A10 A10 A9 A9 A8 A8 A6 A6 A7 A7 SILENCE CONFIRM

3 | GND

Adletzberger T. Baghdadi A. Traunmüller P. Waldhäusl D. mshop@ist.ac.at IST Austria from MIT: https://e-vent.mit.edu/

Sheet: 1/1

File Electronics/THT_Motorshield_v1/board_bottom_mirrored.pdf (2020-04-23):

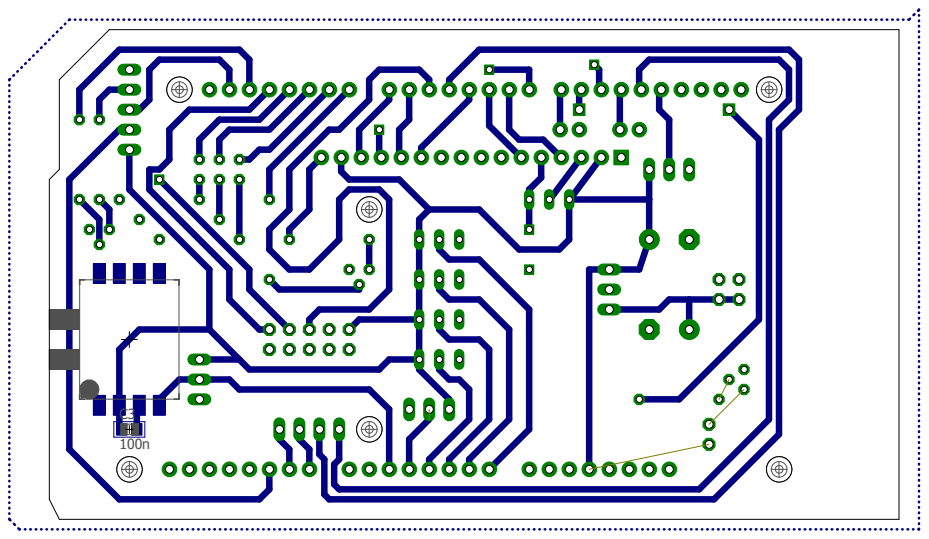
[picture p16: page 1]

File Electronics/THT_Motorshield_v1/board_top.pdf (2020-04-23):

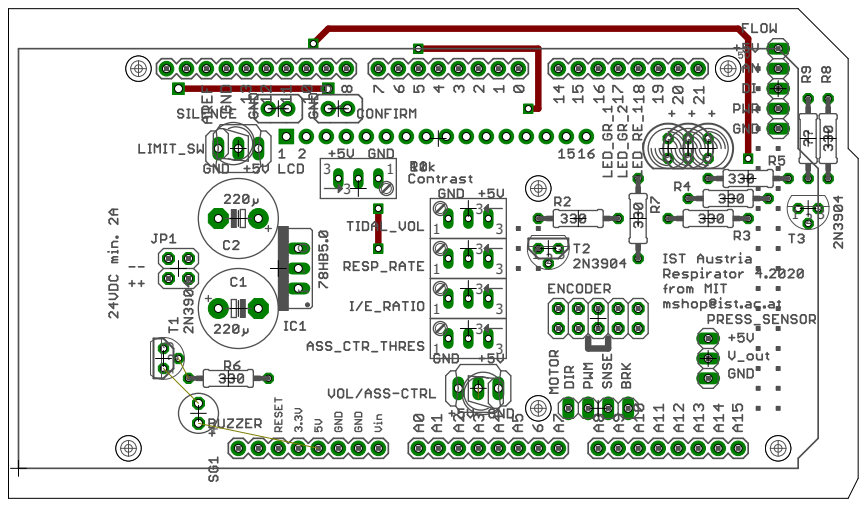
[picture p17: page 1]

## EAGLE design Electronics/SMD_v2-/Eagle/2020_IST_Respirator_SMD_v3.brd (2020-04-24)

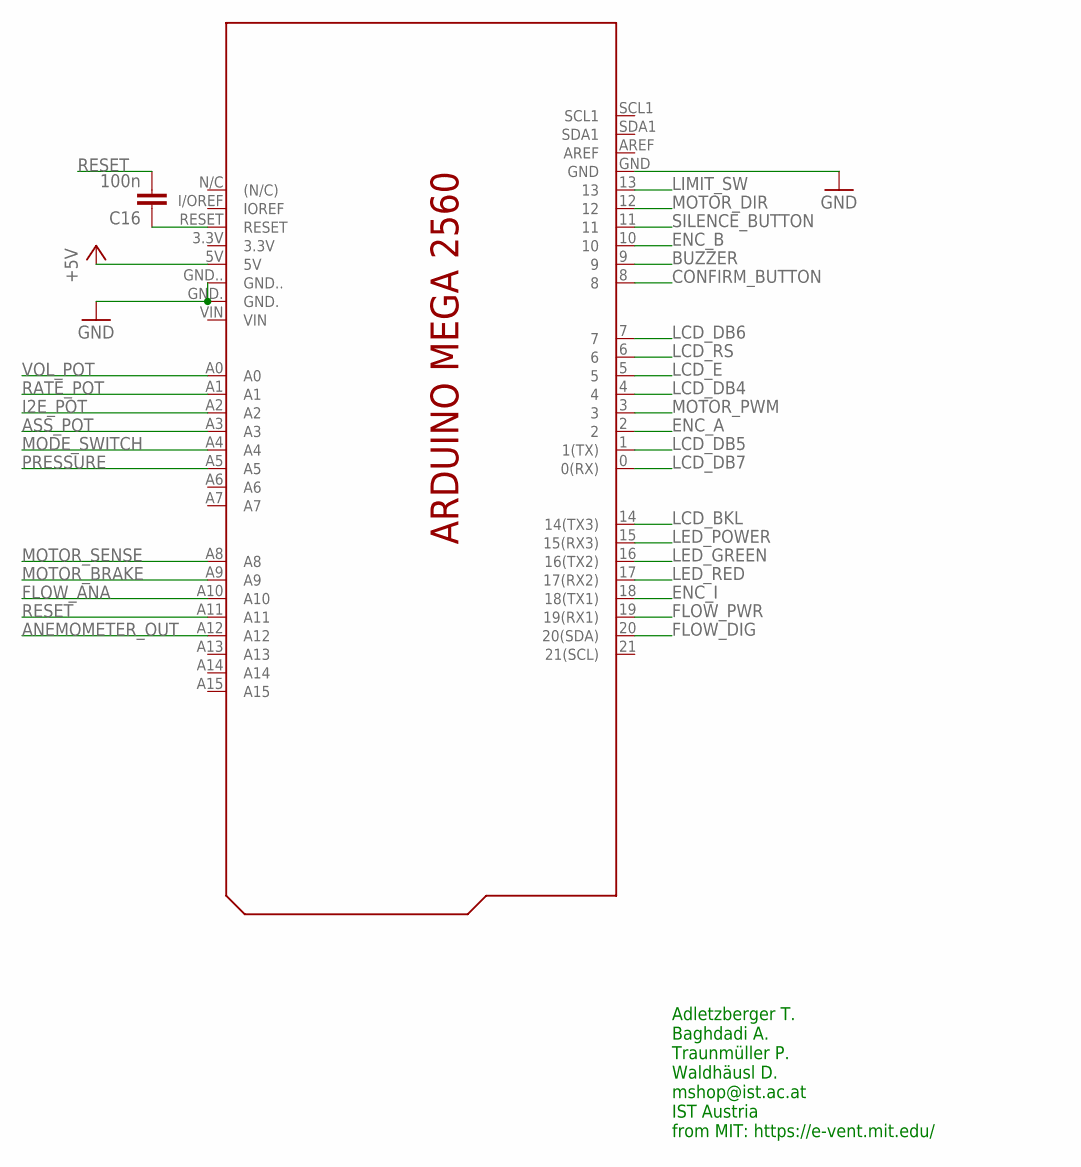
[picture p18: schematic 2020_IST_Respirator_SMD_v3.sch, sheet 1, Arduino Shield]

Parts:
C16: 100n; C0805
PCB1: ARDUINO_MEGA2560_NOTALLPINS

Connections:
+5V: PCB1.5V; also elsewhere on the board
ANEMOMETER_OUT: PCB1.A12
ASS_POT: PCB1.A3; also elsewhere on the board
BUZZER: PCB1.9; also elsewhere on the board
CONFIRM_BUTTON: PCB1.8; also elsewhere on the board
ENC_A: PCB1.2; also elsewhere on the board
ENC_B: PCB1.10; also elsewhere on the board
ENC_I: PCB1.18 (18(TX1)); also elsewhere on the board
FLOW_ANA: PCB1.A10; also elsewhere on the board
FLOW_DIG: PCB1.20 (20(SDA)); also elsewhere on the board
FLOW_PWR: PCB1.19 (19(RX1)); also elsewhere on the board
GND: PCB1.GND, PCB1.GND., PCB1.GND..; also elsewhere on the board
I2E_POT: PCB1.A2; also elsewhere on the board
LCD_BKL: PCB1.14 (14(TX3)); also elsewhere on the board
LCD_DB4: PCB1.4; also elsewhere on the board
LCD_DB5: PCB1.1 (1(TX)); also elsewhere on the board
LCD_DB6: PCB1.7; also elsewhere on the board
LCD_DB7: PCB1.0 (0(RX)); also elsewhere on the board
LCD_E: PCB1.5; also elsewhere on the board
LCD_RS: PCB1.6; also elsewhere on the board
LED_GREEN: PCB1.16 (16(TX2)); also elsewhere on the board
LED_POWER: PCB1.15 (15(RX3)); also elsewhere on the board
LED_RED: PCB1.17 (17(RX2)); also elsewhere on the board
LIMIT_SW: PCB1.13; also elsewhere on the board
MODE_SWITCH: PCB1.A4; also elsewhere on the board
MOTOR_BRAKE: PCB1.A9
MOTOR_DIR: PCB1.12; also elsewhere on the board
MOTOR_PWM: PCB1.3; also elsewhere on the board
MOTOR_SENSE: PCB1.A8; also elsewhere on the board
unnamed: C16.1, PCB1.RESET
PRESSURE: PCB1.A5; also elsewhere on the board
RATE_POT: PCB1.A1; also elsewhere on the board
RESET: C16.2, PCB1.A11
SILENCE_BUTTON: PCB1.11; also elsewhere on the board
VOL_POT: PCB1.A0; also elsewhere on the board

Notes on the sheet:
Adletzberger T. Baghdadi A. Traunmüller P. Waldhäusl D. mshop@ist.ac.at IST Austria from MIT: https://e-vent.mit.edu/

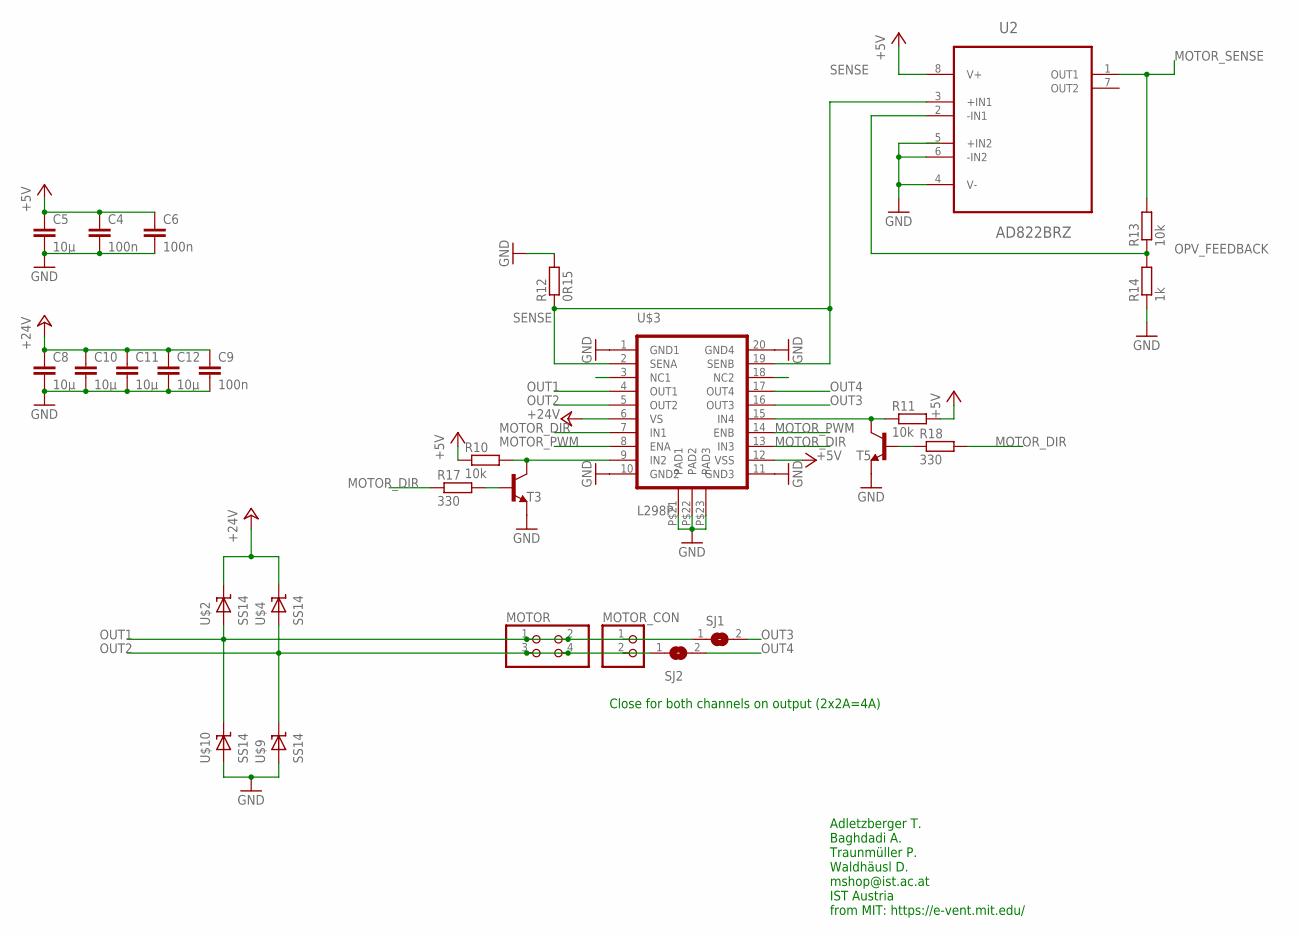
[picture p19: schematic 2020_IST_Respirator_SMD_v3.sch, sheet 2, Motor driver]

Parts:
C4, C6, C9: 100n; C0805
C5, C8, C10, C11, C12: 10µ; C1210
MOTOR: PINHD-2X2; 2X02
MOTOR_CON: PINHD-1X2_3.93MM; 1X02_3.96MM
R10, R11, R13: 10k; R0805
R12: 0R15; R1206
R14: 1k; R0805
R17, R18: 330; R0805
SJ1, SJ2: SJ
T3, T5: MMBT3904LT1-NPN-SOT23-BEC; SOT23-BEC
U2: AD822BRZ; SOIC127P600X175-8N
U$2, U$4, U$9, U$10: SS14; SMA
U$3: L298P; POWER-SO20

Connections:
+5V: C4.1, C5.1, C6.1, R10.1, R11.2, U2.8 (V+), U$3.P$12 (VSS); also elsewhere on the board
+24V: C8.1, C9.1, C10.1, C11.1, C12.1, U$2.P$1 (K), U$3.P$6 (VS), U$4.P$1 (K); also elsewhere on the board
DRIVER_IN2: R10.2, T3.C, U$3.P$9 (IN2)
DRIVER_INV4: R11.1, T5.C, U$3.P$15 (IN4)
GND: C4.2, C5.2, C6.2, C8.2, C9.2, C10.2, C11.2, C12.2, R12.2, R14.1, T3.E, T5.E, U2.4 (V-), U2.6 (-IN2), U$3.P$1 (GND1), U$3.P$10 (GND2), U$3.P$11 (GND3), U$3.P$20 (GND4), U$3.P$21 (PAD1), U$3.P$22 (PAD2), U$3.P$23 (PAD3), U$9.P$2 (A), U$10.P$2 (A); also elsewhere on the board
MOTOR_DIR: R17.1, R18.2, U$3.P$7 (IN1), U$3.P$13 (IN3); also elsewhere on the board
MOTOR_PWM: U$3.P$8 (ENA), U$3.P$14 (ENB); also elsewhere on the board
MOTOR_SENSE: R13.2, U2.1 (OUT1); also elsewhere on the board
unnamed: R17.2, T3.B
unnamed: R18.1, T5.B
OPV_FEEDBACK: R13.1, R14.2, U2.2 (-IN1)
OUT1: MOTOR.1, MOTOR.2, MOTOR_CON.1, SJ1.1, U$2.P$2 (A), U$3.P$4 (OUT1), U$10.P$1 (K)
OUT2: MOTOR.3, MOTOR.4, MOTOR_CON.2, SJ2.1, U$3.P$5 (OUT2), U$4.P$2 (A), U$9.P$1 (K)
OUT3: SJ1.2, U$3.P$16 (OUT3)
OUT4: SJ2.2, U$3.P$17 (OUT4)
SENSE: R12.1, U2.3 (+IN1), U$3.P$2 (SENA), U$3.P$19 (SENB)

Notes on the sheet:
Close for both channels on output (2x2A=4A)
Adletzberger T. Baghdadi A. Traunmüller P. Waldhäusl D. mshop@ist.ac.at IST Austria from MIT: https://e-vent.mit.edu/

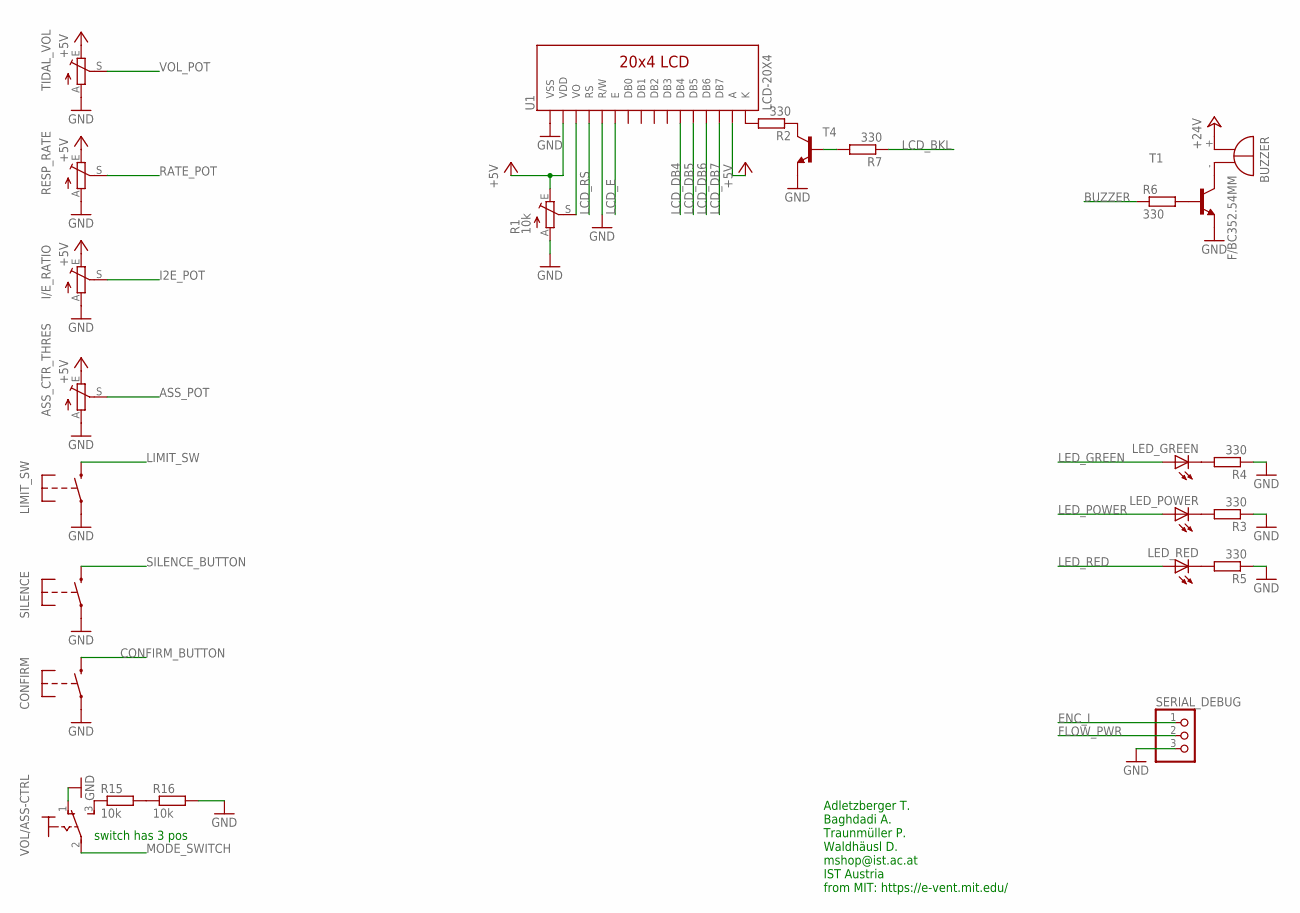
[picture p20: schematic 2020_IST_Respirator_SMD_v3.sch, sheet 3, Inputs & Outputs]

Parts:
ASS_CTR_THRES: TRIM_EU-ROUND; S64W_ROUND-PADS
BUZZER: F/BC352.54MM; F/BC35_2.54MM
CONFIRM: SWITCH-MOMENTARY-22.54; TACTILE-2.54MM
I/E_RATIO: TRIM_EU-ROUND; S64W_ROUND-PADS
LED_GREEN: LED5MM
LED_POWER: LED5MM
LED_RED: LED5MM
LIMIT_SW: SWITCH-MOMENTARY-22.54; TACTILE-2.54MM
R1: 10k; S64W
R2, R3, R4, R5, R6, R7: 330; R0805
R15, R16: 10k; R0805
RESP_RATE: TRIM_EU-ROUND; S64W_ROUND-PADS
SERIAL_DEBUG: PINHD-1X3; 1X03
SILENCE: SWITCH-MOMENTARY-22.54; TACTILE-2.54MM
T1, T4: MMBT3904LT1-NPN-SOT23-BEC; SOT23-BEC
TIDAL_VOL: TRIM_EU-ROUND; S64W_ROUND-PADS
U1: LCD-20X4
VOL/ASS-CTRL: 320-9162.54MM-ROUND-PADS; 320-916:2.54MM:ROUND-PADS

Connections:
+5V: ASS_CTR_THRES.E, I/E_RATIO.E, R1.E, RESP_RATE.E, TIDAL_VOL.E, U1.2 (VDD), U1.15 (A); also elsewhere on the board
+24V: BUZZER.+; also elsewhere on the board
ASS_POT: ASS_CTR_THRES.S; also elsewhere on the board
BUZZER: R6.1; also elsewhere on the board
CONFIRM_BUTTON: CONFIRM.3 (2); also elsewhere on the board
ENC_I: SERIAL_DEBUG.1; also elsewhere on the board
FLOW_PWR: SERIAL_DEBUG.2; also elsewhere on the board
GND: ASS_CTR_THRES.A, CONFIRM.1, I/E_RATIO.A, LIMIT_SW.1, R1.A, R3.1, R4.1, R5.1, R16.2, RESP_RATE.A, SERIAL_DEBUG.3, SILENCE.1, T1.E, T4.E, TIDAL_VOL.A, U1.1 (VSS), U1.5 (R/W), VOL/ASS-CTRL.1 (O); also elsewhere on the board
I2E_POT: I/E_RATIO.S; also elsewhere on the board
LCD_BKL: R7.1; also elsewhere on the board
LCD_DB4: U1.11 (DB4); also elsewhere on the board
LCD_DB5: U1.12 (DB5); also elsewhere on the board
LCD_DB6: U1.13 (DB6); also elsewhere on the board
LCD_DB7: U1.14 (DB7); also elsewhere on the board
LCD_E: U1.6 (E); also elsewhere on the board
LCD_RS: U1.4 (RS); also elsewhere on the board
LED_GREEN: LED_GREEN.A; also elsewhere on the board
LED_POWER: LED_POWER.A; also elsewhere on the board
LED_RED: LED_RED.A; also elsewhere on the board
LIMIT_SW: LIMIT_SW.3 (2); also elsewhere on the board
MODE_SWITCH: VOL/ASS-CTRL.2; also elsewhere on the board
unnamed: BUZZER.-, T1.C
unnamed: R6.2, T1.B
unnamed: R2.1, T4.C
unnamed: R7.2, T4.B
unnamed: R15.1, VOL/ASS-CTRL.3 (S)
unnamed: R15.2, R16.1
unnamed: R2.2, U1.16 (K)
unnamed: R1.S, U1.3 (VO)
unnamed: LED_GREEN.K (C), R4.2
unnamed: LED_POWER.K (C), R3.2
unnamed: LED_RED.K (C), R5.2
RATE_POT: RESP_RATE.S; also elsewhere on the board
SILENCE_BUTTON: SILENCE.3 (2); also elsewhere on the board
VOL_POT: TIDAL_VOL.S; also elsewhere on the board

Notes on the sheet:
Adletzberger T. Baghdadi A. Traunmüller P. Waldhäusl D. mshop@ist.ac.at IST Austria from MIT: https://e-vent.mit.edu/
switch has 3 pos

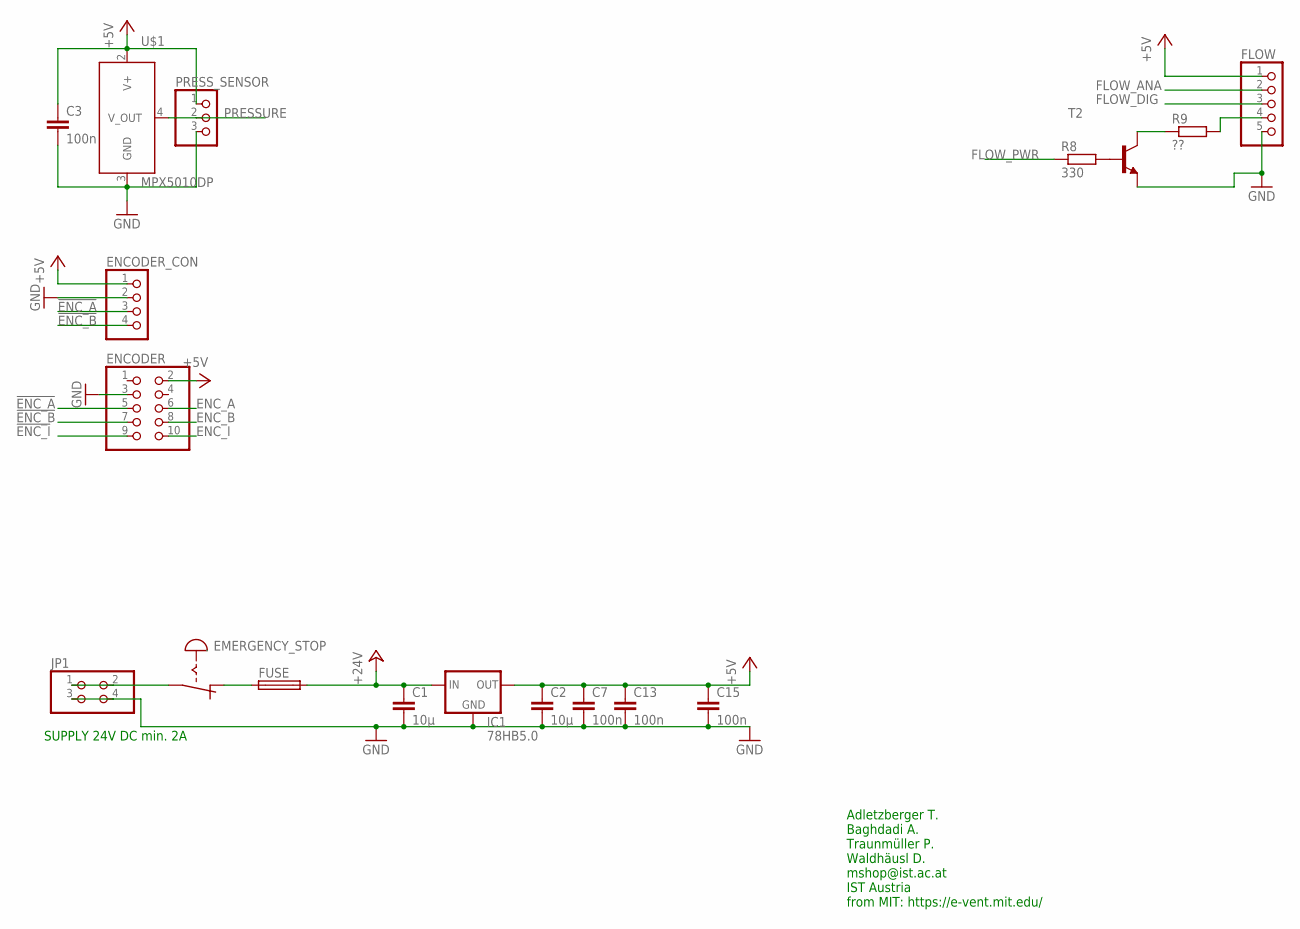
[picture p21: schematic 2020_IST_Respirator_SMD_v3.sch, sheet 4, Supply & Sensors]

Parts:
C1, C2: 10µ; C1210
C3, C7, C13, C15: 100n; C0805
EMERGENCY_STOP: EMERGENCY_STOP; 320-916:2.54MM:ROUND-PAD_2PINS
ENCODER: PINHD-2X5; 2X05
ENCODER_CON: PINHD-1X42MM; 1_04X2MM
FLOW: PINHD-1X5; 1X05
FUSE: SH22,5
IC1: 78HB5.0; R-78HB
JP1: PINHD-2X2; 2X02
PRESS_SENSOR: PINHD-1X3; 1X03
R8: 330; R0805
R9: ??; R0805
T2: MMBT3904LT1-NPN-SOT23-BEC; SOT23-BEC
U$1: MPX5010DP; MPX5010DP_SOP482

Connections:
!ENC_A: ENCODER.5, ENCODER_CON.3
!ENC_B: ENCODER.7, ENCODER_CON.4
!ENC_I: ENCODER.9
+5V: C2.1, C3.1, C7.1, C13.1, C15.1, ENCODER.2, ENCODER_CON.1, FLOW.1, IC1.OUT, PRESS_SENSOR.1, U$1.2 (V+); also elsewhere on the board
+24V: C1.1, FUSE.2, IC1.IN; also elsewhere on the board
ENC_A: ENCODER.6; also elsewhere on the board
ENC_B: ENCODER.8; also elsewhere on the board
ENC_I: ENCODER.10; also elsewhere on the board
FLOW_ANA: FLOW.2; also elsewhere on the board
FLOW_DIG: FLOW.3; also elsewhere on the board
FLOW_PWR: R8.1; also elsewhere on the board
GND: C1.2, C2.2, C3.2, C7.2, C13.2, C15.2, ENCODER.3, ENCODER_CON.2, FLOW.5, IC1.GND, JP1.3, JP1.4, PRESS_SENSOR.3, T2.E, U$1.3 (GND); also elsewhere on the board
unnamed: R8.2, T2.B
unnamed: R9.1, T2.C
unnamed: FLOW.4, R9.2
unnamed: EMERGENCY_STOP.2, JP1.1, JP1.2
unnamed: EMERGENCY_STOP.1, FUSE.1
PRESSURE: PRESS_SENSOR.2, U$1.4 (V_OUT); also elsewhere on the board

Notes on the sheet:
SUPPLY 24V DC min. 2A
Adletzberger T. Baghdadi A. Traunmüller P. Waldhäusl D. mshop@ist.ac.at IST Austria from MIT: https://e-vent.mit.edu/

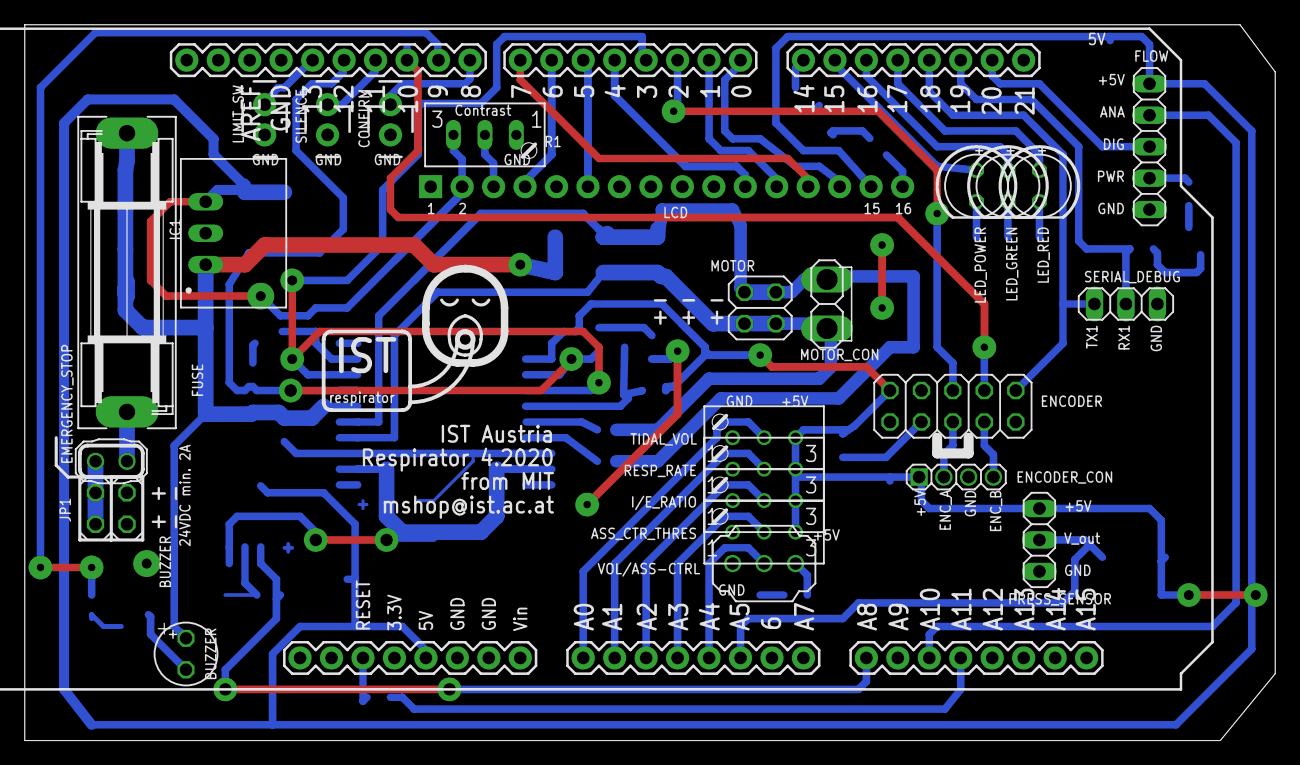
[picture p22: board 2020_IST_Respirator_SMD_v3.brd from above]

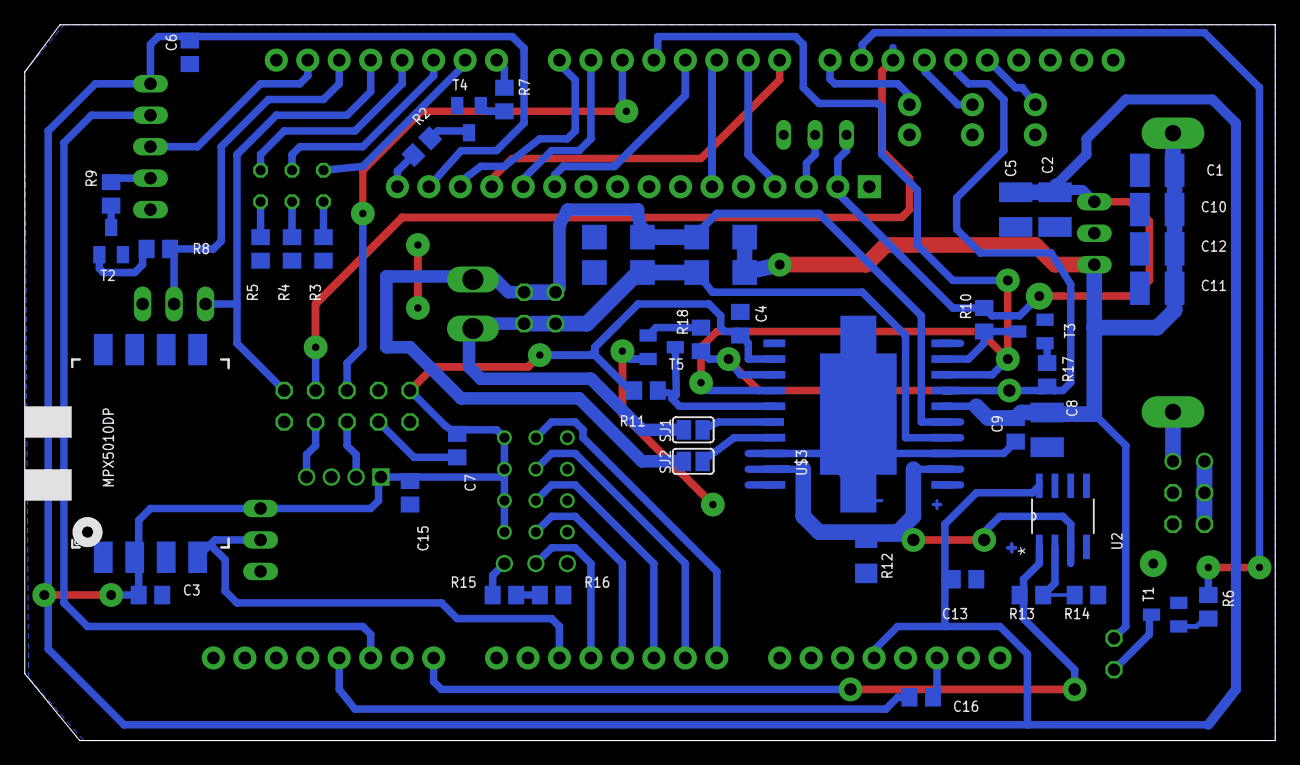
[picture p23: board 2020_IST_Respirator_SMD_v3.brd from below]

Board: 2 copper layers, 101.0 x 57.8 mm, 72 parts (46 on the bottom side), 62 nets.

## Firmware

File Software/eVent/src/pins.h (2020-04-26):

//analog sensors
#define PRESSURE A5       //(922-7409), analog 0.2-4.7V, 0-1019.78mmH2O

#define LIMIT_SWITCH   13     //limit switch for homing

//control potentiometers, single turn 10k, analog 0-5V (789-9438)
#define VOL_POT A0            //sets volume setpoint in ml
#define RATE_POT A1           //sets breaths per minute 5-40 BPM
#define I2E_POT A2            //sets inspiration/expiration time ratio 1:1 - 1:4
#define PRS_POT A3            //sets max pressure

//switches and buttons
#define MODE_SWITCH A4         //selects volume or assist control
#define SILENCE_BUTTON 11         // momentary button to mute alarms
#define CONFIRM_BUTTON  8          // momentary buttton to confirm potentiometer changes

//OUTPUTS
#define BUZZER      9             //piezo buzzer (724-3178) PWM

//Display
#define LCD_RS      6
#define LCD_ENABLE  5
#define LCD_D4      4
#define LCD_D5      1
#define LCD_D6      7
#define LCD_D7      0
#define LCD_BACKLIGHT 14


//Encoder
#define ENC_A   2
#define ENC_B   10
#define ENC_I   18

//Leds
#define LED_POWER 15
#define LED_GREEN 16
#define LED_RED 17

#define RESET_PIN A11

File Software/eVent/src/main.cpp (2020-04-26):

#include <Arduino.h>
#include "pins.h"
#include "states.h"
#include "display.h"
#include "modes.h"
#include "globalFlags.h"
#include "../lib/Encoder_ID129/Encoder.h"
#include "alarms.h"

//for Arduino MEGA with compatibility to UNO for essential functions

bool PRESSURE_FLAG;
bool CHANGES_FLAG;
bool START_UP_FLAG;
bool SILENCE_FLAG;
bool VOLUME_FLAG;


const int diffBagPosition = 60;     //ticks between homePosition and fingers touching the bag (HARDCODED)
const int timeHold = 200;           //The amount of time (in milliseconds) to hold the compression at the end of the inhale for plateau pressure
const int velocityHoming = 70;      //slow speed for homing
const int controlPeriod = 50;       //ms
const int closePosition = 190;      //Ticks between home and full close

//state machine variables
int lastMode;
int mode;                 // switch state variable for outer switch
int nextMode;             // mode to be executed after homing
int state;                // switch state variable for inner switch

//In/Exhale times
int targetTimeInhale;     // The length of time (in ms) of the inspiratory phase.
int targetTimeExhale;     // The length of time (in ms) of the expiratory phase.

//volume parameters
int volumeTidal;          // The total volume of air to be delivered to the patient
int volumeTicks;          // The number of Encoder ticks required for the given volumeTidal
int realVolume;
int realVolumeTicks;

//rate and ratio
int breathsPerMinute;     // Breaths per minute, also called respiratory rate (RR). Typically varies between 8-30 BPM.
float I2E_ratio;          // The ratio of the duration of the inhale to the duration of the exhale.

//velocity control
float targetInhaleVelocity; //target input of controller
float targetExhaleVelocity; //target input of controller
int currentVelocity;        //Measure Input of controller.
int dutyCycleOutput;       //Output of controller. The inhale velocity scaled from 0-255 for PWM Output
int integral;
float iTerm;   //integral term of PI controller
float pTerm;

//flow
int currentFlow;        //ml/s
int targetFlow;
int meanFlow;
int maxFlow;

//pressures
int pressurePlateau;      //Last measured plateauPressure in mbar
int limitPressure;        //maximum presssure for pressure limited mode

//variables for setpoint potentiometers
int volumeTidalSet;       //Current potentiometer value for volumeTidal, not confirmed
int breathsPerMinuteSet;  //Current potentiometer value for breathsPerMinute, not confirmed
float I2E_ratioSet;       //Current potentiometer value for I2E_ratio, not confirmed
int limitPressureSet;     //Current potentiometer value for limitPressure, not confirmed
int lastVolumeTidalSet;       //last potentiometer value for volumeTidal, not confirmed
int lastBreathsPerMinuteSet;  //last potentiometer value for breathsPerMinute, not confirmed
float lastI2E_ratioSet;       //last potentiometer value for I2E_ratio, not confirmed
int lastLimitPressureSet;//last potentiometer value for limitPressure, not confirmed



//timers in ms
unsigned long timerSetPoint;
unsigned long timerPotentiometer;
unsigned long timerDebounce;
unsigned long timerDisplay;
unsigned long timerControlPeriod;
unsigned long timerInhale;
unsigned long timerExhale;
unsigned long timerDelay;
unsigned long timerRealInhale;
unsigned long timerRealExhale;
unsigned long timerSilence;
unsigned long timerAlarmsInterrupt;

int currentMeanFlow;

int controlCounter;
long plottingCounter;

//encoder instance
Encoder encoder(ENC_A,ENC_B);

void calculateVolumeParameters(){
  int singleBreathTime =60000/breathsPerMinute - timeHold;
  targetTimeInhale = singleBreathTime*I2E_ratio;
  targetTimeExhale = singleBreathTime -targetTimeInhale;
  volumeTicks = (volumeTidal+420)/12; //linear model y=12*x-420
  inhaleEndPosition = bagPosition - volumeTicks;
  meanFlow = (volumeTicks/(targetTimeInhale/1000.0))*12;
  targetExhaleVelocity = volumeTicks/(targetTimeExhale/1000.0);
}

int getPressure(){

  int readingA = analogRead(PRESSURE);
  delay(5);
  int readingB = analogRead(PRESSURE);
  delay(5);
  int readingC = analogRead(PRESSURE);
  return map((readingA+readingB+readingC)/3, 40, 963, 0, 100); // from 0.2V (41) to 3.7V (963) to a range of 0 to 100mbar
}


void controlInhaleVelocity(){

  //calculate ticks in last period
  int ticksInLastPeriod = prePeriodPosition-currentPosition;
  //calculate current velocity in Ticks/s
  currentVelocity =  ticksInLastPeriod * (1000/controlPeriod); //current velocity in Ticks/s

  //flow calculation
  //two seperate linear apprxomiations are used <60 or >60
  //calculate current flow in ml/s
  if((bagPosition-prePeriodPosition) < 60){
    currentFlow = currentVelocity*8;
  }
  else{
    currentFlow = currentVelocity*12;
  }
  currentMeanFlow = (currentMeanFlow*0.6+currentFlow*0.4);

  if(mode == MODE_VOLUME){
    //calculate target flow
    int inhaleControlCycles = targetTimeInhale/controlPeriod;
    if(controlCounter < inhaleControlCycles/2){
      targetFlow = meanFlow * ((1.1*controlCounter)/(inhaleControlCycles/2.0)+0.2);      //1.1 -> 110% difference between 20% at begin and 130% at the end
    }
    else{
      targetFlow = 1.3*meanFlow;            //130% flow in second half to reach mean flow
    }

  }

if((bagPosition-currentPosition) < 60){
  targetInhaleVelocity = targetFlow/8;
}
else{
  targetInhaleVelocity = targetFlow/12;
}
  //controller
  int controlDifference = targetInhaleVelocity - currentVelocity;
  //define P term of controller
  if(controlDifference < 0){
    pTerm = 0.001;
  }
  else{
    pTerm = 0.07;
  }
  iTerm = 0.001;
  integral += controlDifference;

  //new inhalleVelocity
  dutyCycleOutput = dutyCycleOutput + controlDifference*pTerm + integral*iTerm;
  //limit for inhale velocity
  if(dutyCycleOutput > 255){
    dutyCycleOutput=255;
  }
  //set parameters for next control cycle
  controlCounter++;
  prePeriodPosition = currentPosition;
}

void controlExhaleVelocity(){

  //calculate ticks in last period
  int ticksInLastPeriod = currentPosition - prePeriodPosition;
  //calculate current velocity in Ticks/s
  currentVelocity =  ticksInLastPeriod * (1000/controlPeriod); //current velocity in Ticks/s

  //controller
  int controlDifference = targetExhaleVelocity -currentVelocity;

  if(controlDifference < 0){
    pTerm = 0.001;
  }
  else{
    pTerm = 0.08;
  }
  iTerm = 0.0001;
  integral += controlDifference;

  dutyCycleOutput = dutyCycleOutput + controlDifference*pTerm + integral*iTerm;

  if(dutyCycleOutput < 35){
    dutyCycleOutput = 35;
  }
  //limit for inhale velocity
  if(dutyCycleOutput > 40){
    dutyCycleOutput=40;
  }
}

void controlPressure(){

  int currentPressure = getPressure();
  int controlDifference = limitPressure - currentPressure;
  integral += controlDifference;
  pTerm = 2;
  if(controlCounter < 4){
    integral = 0;
  }
  iTerm = 0.1;

  //new inhalleVelocity
  dutyCycleOutput = dutyCycleOutput + controlDifference*pTerm + integral*iTerm;
  //limit for inhale velocity
  if(dutyCycleOutput > 255){
    dutyCycleOutput=255;
  }
  if(currentPosition < (homePosition - closePosition)){
    timerInhale = millis()-1; //stops
  }

  //set parameters for next control cycle
  controlCounter++;
  prePeriodPosition = currentPosition;
}

void timer1_setup(long time_in_ms) {
   // initialize timer1
  noInterrupts();           // disable all interrupts
  TCCR1A = 0;
  TCCR1B = 0;
  TCNT1  = 0;
  unsigned long long match_register_value = 62500*(time_in_ms/1000.0); // compare match register 16MHz/256/xHz
  OCR1A = match_register_value;            // compare match register 16MHz/256/x Hz
  //OCR1A = 31250;
  TCCR1B |= (1 << WGM12);   // CTC mode
  TCCR1B |= (1 << CS12);    // 256 prescaler
  TIMSK1 |= (1 << OCIE1A);  // enable timer compare interrupt
  interrupts();             // enable all interrupts
}

ISR(TIMER1_COMPA_vect)          // timer1 interrupt service routine
{
  handleAlarms(mode, pressurePlateau, getPressure(), encoder.read(), (realVolume/1000.0*breathsPerMinute));
}

void setup() {
  pinMode(RESET_PIN, OUTPUT);
  digitalWrite(RESET_PIN, HIGH);
  pinMode(PRESSURE, INPUT);
  pinMode(LIMIT_SWITCH, INPUT);
  pinMode(VOL_POT, INPUT);
  pinMode(RATE_POT, INPUT);
  pinMode(I2E_POT, INPUT);
  pinMode(PRS_POT, INPUT);
  pinMode(MODE_SWITCH, INPUT_PULLUP);
  pinMode(SILENCE_BUTTON, INPUT_PULLUP);
  pinMode(CONFIRM_BUTTON, INPUT_PULLUP);
  pinMode(BUZZER, OUTPUT);
  pinMode(LCD_BACKLIGHT, OUTPUT);
  pinMode(ENC_A, INPUT_PULLUP);
  pinMode(ENC_B, INPUT_PULLUP);
  pinMode(ENC_I, INPUT_PULLUP);
  pinMode(LED_POWER, OUTPUT);
  pinMode(LED_GREEN, OUTPUT);
  pinMode(LED_RED, OUTPUT);

  START_UP_FLAG = true;

  //debugging serial
  Serial1.begin(9600);
  //lcd
  initLCD();
  homeScreen();
  digitalWrite(LCD_BACKLIGHT, HIGH);

  //test outputs
  digitalWrite(LED_POWER, HIGH);
  digitalWrite(LED_GREEN, HIGH);
  digitalWrite(LED_RED, HIGH);
  tone(BUZZER, 10000);
  delay(1500);
  digitalWrite(LED_POWER, LOW);
  digitalWrite(LED_GREEN, LOW);
  digitalWrite(LED_RED, LOW);
  noTone(BUZZER);

  //inital states
  lastMode = MODE_IDLE;
  mode = MODE_IDLE;
  nextMode = MODE_IDLE;
  state = 0;
  realVolume = 500;
  pressurePlateau = 5;

  timer1_setup(250); // perform safety and alarn function every 250ms
  digitalWrite(LED_POWER, HIGH);    //LED to show that arduino is running
}
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

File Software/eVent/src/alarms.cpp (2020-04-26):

#include "pins.h"
#include <Arduino.h>
#include "globalFlags.h"
#include "modes.h"
#include "states.h"
#include "alarms.h"

const int pressurePlateauMax = 30;  // The maximum plateau pressure to start the alarm.
const int pressureMax = 40;         // [mBar] The maximum pressure for inhale to start the alarm.
const int pressureMin = 5;          // [mBar] The minimum pressure for inhale to start the alarm. (Leakage)
const int minVolumeperMinute = 3.0; // Liters

unsigned long timerBlink;

void handleAlarms(int mode, int pressurePlateau, int pressure, int position,
                  float volumePerMiunute) {   // volumePerMiunute in L/min
  // safety functions -----------------------------------------------------------
  // min volume in pressure mode
  if(volumePerMiunute < minVolumeperMinute && mode == MODE_PRESSURE){
    VOLUME_FLAG = true;
  }
  else{
    VOLUME_FLAG = false;
  }

  //pressure
  PRESSURE_FLAG = ((pressure > pressureMax) || (pressurePlateau > pressurePlateauMax)
                   || (pressurePlateau < pressureMin));

  // alarm handling--------------------------------------------------------------

  if(CHANGES_FLAG){
    if(millis() > timerBlink){
      digitalWrite(LCD_BACKLIGHT, !digitalRead(LCD_BACKLIGHT));
      timerBlink = millis() + 500;
    }
  }

  if((PRESSURE_FLAG || VOLUME_FLAG)){
    if(!SILENCE_FLAG){
      tone(BUZZER, 10000, 500);
    }
    digitalWrite(LED_RED, HIGH);
  }
  else{
    noTone(BUZZER);
    digitalWrite(LED_RED, LOW);
  }

  // avoid overflow of millis
  if(millis() > 4233600000){        // 49days
    digitalWrite(RESET_PIN, LOW);
  }
}

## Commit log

2020-04-24 Adding the SMD version of circuit
2020-04-24 Adding the SMD version of circuit & updating user manual
2020-04-24 Updated SMD v3, added gerbers and board pdfs
    [2020_IST_Respirator_SMD_v3.brd, 2020_IST_Respirator_SMD_v3.sch, 2020_IST_Respirator_v1.1.brd, 2020_IST_Respirator_v1.1.sch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]
2020-04-26 Remove motor code to use software for alarms and monitoring using only pressure sensor
2020-04-26 Remove more motor code and fix lint error

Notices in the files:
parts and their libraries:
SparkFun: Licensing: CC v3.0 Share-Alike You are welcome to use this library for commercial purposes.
